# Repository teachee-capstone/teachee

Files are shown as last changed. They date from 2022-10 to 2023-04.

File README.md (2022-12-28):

# TeachEE
This monolithic repository contains all software, RTL, hardware designs, and
reports for the TeachEE oscilloscope capstone project.

Each subdirectory of this repository contains a README explaining its contents.
The repository primarily consists of the software, hardware and rtl
subdirectories. These folders contain the Rust desktop app code, PCB design, and
SystemVerilog code respectively. In addition to these directories, there are also dedicated folders for our reports and miscellaneous files.

# Authors
- [Eric Yang](https://github.com/EYangster)
- [John Giorshev](https://github.com/jagprog5)
- [Timothy Morland](https://github.com/thetimmorland)
- [Ethan Peterson](https://github.com/ethanmpeterson)

# System Block Diagram

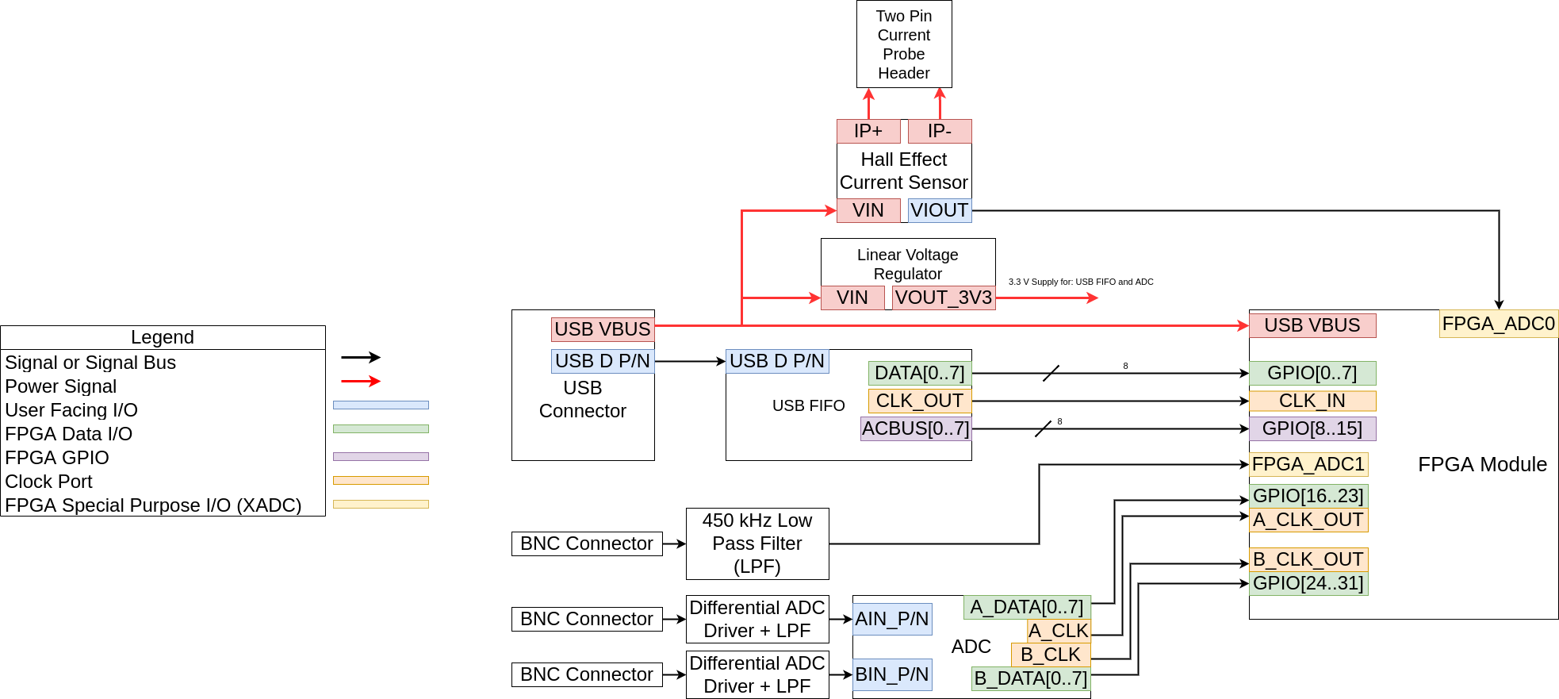
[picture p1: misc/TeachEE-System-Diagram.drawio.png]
Drawio Diagram


# PCB Design
The full design has been uploaded to Altium's online viewer. Click [here](https://365.altium.com/files/0E0F9283-7CE6-4F7A-A1F5-A4D0804C79EE) for
full schematics, layout, and bill of materials.

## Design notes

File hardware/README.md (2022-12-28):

# TeachEE Hardware

The hardware folder is broken down as follows:
- The TeachEE directory contains the Altium schematic and layout files.
- Vendor Communications contains the DFM/DFA related correspondence we had with
  the vendor. (Bittle / 7PCB.com)
- The prints folder holds a variety of reference PDFs including prints of the
  schematics and layout.

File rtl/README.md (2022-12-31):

# TeachEE RTL
This folder contains all the SystemVerilog code for the CMOD A7 35-T FPGA Module
installed on the TeachEE PCB. The subdirectories hold RTL modules for the
oscilloscope firmware as well as some example Vivado projects demonstrating each
module.

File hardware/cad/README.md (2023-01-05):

# CAD
This folder contains the Fusion 360 CAD for the TeachEE PCB enclosure. Currently, it is a simple 3D printed back plate to ensure that board is supported and not exposed to any short circuits when placed on metal surfaces.

The PCB is attached to the tray using M3 screws and heat-set inserts in the tray. Links to the parts are provided below:

- [Heat-set inserts](https://3dprintingcanada.com/products/m3x5-heat-set-brass-knurled-insert-nut-10-pack?variant=39417926451269&ab_version=B&gclid=Cj0KCQiA5NSdBhDfARIsALzs2ECMH8QoEQ02sKMftqXC5ZgHy1LyS_iIIELi0KJeUmQRDeO0tNmDuHEaArR1EALw_wcB)
- [M3x6 Screws](https://www.mouser.ca/ProductDetail/Keystone-Electronics/7689-1?qs=wOxb8XianXi8JqFIUmvR9Q%3D%3D&mgh=1&gclid=Cj0KCQiA5NSdBhDfARIsALzs2EC01tEHi3BZq6HwX3hLjHV2irnkbD29NnEpqoeVlWQxZYohotHjxuUaArSlEALw_wcB)

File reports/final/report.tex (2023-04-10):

\documentclass[letterpaper,11pt]{article}
\usepackage[parfill]{parskip} % Remove paragraph indentation
\usepackage{amsmath}
\usepackage{float}
\usepackage[margin=1in]{geometry}
\usepackage{graphicx}
\usepackage{placeins}
\usepackage{siunitx}
\usepackage[title]{appendix}
\usepackage{pdflscape}
\usepackage{tabularx}
\usepackage{times}
\usepackage{url}
\usepackage{setspace}
\usepackage[none]{hyphenat}
\usepackage{pdfpages}
\usepackage{longtable}
\usepackage{tikz}
\usepackage{hyperref}
\usepackage{minted}

\DeclareSIUnit{\samplepersec}{SPS}
\newcommand{\code}[1]{\mintinline{text}{#1}}

\begin{document}

\begin{titlepage}
    \begin{center}
        \vspace*{1cm}

        \Large
        \textbf{ELEC 490/498 Project Final Report}

        \vspace{0.5cm}
        Group 18\\
        TeachEE: Accessible Electronics Instrumentation\\
        \vspace{0.5cm}
        \normalsize
        \textbf{John Giorshev (20103586, john.giorshev@queensu.ca) \\ Eric Yang (20120750, e.yang@queensu.ca) \\ Ethan Peterson (20105011, 17emp5@queensu.ca) \\ Timothy Morland (20096286, 17tm22@queensu.ca)}\\
        \vspace{0.5cm}
        Submitted April 10, 2023\\

        \vfill
            
        \textbf{To:}\\
        Instructor Dr. Michael Korenberg (korenber@queensu.ca) \\
        Instructor Dr. Alireza Bakhshai (alireza.bakhshai@queensu.ca) \\
        Instructor Dr. Alex Tait (alex.tait@queensu.ca) \\
        Instructor and Supervisor Dr. Sean Whitehall (sw109@queensu.ca) \\
        Supervisor Dr. Thomas Dean (tom.dean@queensu.ca) \\
            
        \vspace{1.8cm}

    \end{center}
\end{titlepage}
\setstretch{1.5}
\pagenumbering{gobble}
\section*{Executive Summary}
% ERIC OWNS THIS SECTION
The Covid-19 pandemic abruptly forced educational institutions towards online
learning. As a result, many of these institutions were unequipped to deal with
this new learning model. Much of the onsite equipment, such as oscilloscopes and
signal generators, is ill-suited for online learning due to its high cost and
poor portability. Additionally, the take-home equipment provided to students
during the pandemic was typically of lower quality in comparison. In particular,
the oscilloscopes provided by the Electronics II course taught at Queen's
University were expensive and of poor quality. They had tiny 3-inch displays and
a small maximum bandwidth of 100 kHz. Moreover, they were single channel,
limiting the student's ability to see how signals in a circuit are related to
one another.

TeachEE is a general-purpose electronics measurement instrument designed for remote
engineering labs, functioning as both an oscilloscope and current monitor. It bundles
together the functionality most required in Electrical Engineering labs and packages
it with lightweight and portable software. 

TeachEE's hardware consists of a four-layer custom designed Printed Circuit
Board (PCB) powered by a USB connection to the computer. The PCB has a
two-channel 1 MSPS ADC for reading low-speed signals and current from a
hall-effect sensor. The PCB also has a two-channel 40 MSPS Analog to Digital
Converted (ADC) for observing high speed signals. Both ADCs are connected to a
Field Programmable Gate Array (FPGA), which is in turn connected to USB 2.0 PHY.
The FPGA collects sample data from both ADCs and frames it into packets, which
are sent over the USB PHY and transmitted to the computer to be decoded and
displayed. This allows TeachEE to leverage the student's machine to create a
streamlined user experience. 

TeachEE's software is a full stack application written in Rust. Its workload is split
between three modules, each of which runs in its own thread. The first module is the
USB Manager, responsible for reading and decoding packets from the hardware driver
into voltage and current samples. The second is the App, responsible for updating and
displaying the user interface. The third module, the Controller, facilitates
communication between the two, and performs signal triggering and frequency spectrum
analysis. These three threads pass samples between each other using two sets of two
buffers: the USB Buffers and App Buffers. By cycling between buffers within a set,
much of the data processing can be parallelized, greatly improving performance. 

\newpage

\setstretch{1}
\tableofcontents
\listoffigures
\listoftables
\newpage
% upgraded this to double spacing as per report formatting reqs
\setstretch{2}
\pagenumbering{arabic}
\section{Motivation \& Background}
% ERIC
% Motivation and background – a clear problem statement and the motivation for the
% project (why is it technologically interesting?). A good motivation argument
% usually relies on facts and figures about the technological void that you seek
% to fill with your design. Back-up your facts and figures by referencing archival
% references. Examples of archival references include: journal papers, conference
% papers, patents, books, corporate technical and annual reports, application
% notes. Use the standard IEEE citation format. Website URLs are not archival
During the Covid-19 pandemic, universities abruptly switched to remote learning
as campuses were shut down. This sudden change exposed the lack of support for
digital learning models \cite{online_learning}. Although the pandemic has since
passed, forward-thinking institutions are starting to invest in online programs,
for example, by leveraging AI chatbots and teaching assistants. Additionally,
online course providers such as Udemy have recently risen in popularity as a
cheap alternative to traditional postsecondary education. With this trend of
remote higher education, engineering students will need their own lab equipment
to complete their learning requirements.

TeachEE is a general-purpose electronics measurement instrument
designed for remotely delivered engineering labs. It acts as both a
USB oscilloscope and current monitor. Currently, there are few instrumentation
options for students completing their labs remotely. The oscilloscopes used for
onsite learning are bulky and difficult to use. TeachEE bundles
together the functionality most commonly required for electrical engineering
labs and packages it with portable software that can run on lower end computers
with any operating system.

As TeachEE is targeted for electrical engineering students, it must be powerful
enough for use in a variety of practices, but also simple and intuitive enough
for novices. It must be compact, to be carried between classes, and
operating-system agnostic, to ensure that students can use it with any machine.
Finally, TeachEE must be cost-efficient, so that students can justify purchasing
this oscilloscope as opposed to alternatives.

\section{Design}
%% Design – describe your functional requirements and constraints; provide
%% technical details about your design process for meeting the project goals;
%% this might include identifying subsystems, analysis, modeling, and key
%% decisions made. If your project involves circuit design, you should describe
%% the simulations used to create your design

% Summarize Design process of hardware, fpga and SW. Make a brief note about how
% we parallelized much of the work by modelling the data as a byte stream.
% allowing for significant dev work without physical HW in house.

The TeachEE design is derived from the system requirements set in the blueprint
report. Given in Table \ref{tab:hw-reqs} and \ref{tab:sw-reqs} are the most important hardware
and software requirements respectively. It should also be noted that the FPGA
shares responsibility with the desktop application for fulfilling software
requirements.

\begin{table}[H]
    \caption{Hardware Requirements}
    \begin{tabularx}{\textwidth}{l|l|l|l}
          & Specification & Target Value & Tolerance \\
        \hline
        1 &Voltage Input Bandwidth&\SI{100}{\kilo\hertz}& $\pm \SI{1}{\kilo\hertz}$ \\
        2 &Current Input Bandwidth&\SI{100}{\kilo\hertz}& $\pm \SI{1}{\kilo\hertz}$ \\
        3 &Number of Current Input Channels& $1$ & $0$ \\ 
        4 &Number of Voltage Input Channels& $1$ & $+2$ \\
        5 &Voltage Sample Rate& \SI{1}{\mega\samplepersec} & \SI{0}{\mega\samplepersec}\\
        6 &Current Sample Rate& \SI{1}{\mega\samplepersec} & \SI{0}{\mega\samplepersec} \\
    \end{tabularx} 
\label{tab:hw-reqs}
\end{table}

\begin{table}[H]
  \caption{Software Requirements}
  \begin{tabularx}{\textwidth}{l|l}
    \textbf{1} & \textbf{Functional Requirements}\\
    \hline
    1.1 & The software shall be able to modify the horizontal and vertical scales of the plot. \\
    1.2 & The software shall be able to modify the trigger voltage. \\
    1.3 & The application shall be deployable to Windows, macOS, and Linux. \\
    \hline
    \textbf{2} & \textbf{Interface Requirements} \\
    \hline
    2.1 & The software shall be able to capture voltage samples and export them to a CSV file. \\
    2.2 & The software shall receive samples via the FTDI 232 in synchronous mode. \\
    \hline
    \textbf{3} & \textbf{Performance Requirements} \\
    \hline
    3.1 & The software shall be able to render waveforms at a rate of \SI{30}{\hertz} on screen.
  \end{tabularx} 
  \label{tab:sw-reqs}
\end{table}

Based on the system requirements, the project is divided into three
subsystems; hardware, FPGA, and software. The following subsections correspond
to each subsystem, each describing the subsystem's top level design and
key design decisions made to comply with system requirements.

% INCLUDE THE BLOCK DIAGRAMS FOR EACH OF THESE
% Talk about old design (from blueprint)
\subsection{Hardware} % Ethan
The primary design driving requirements for the Printed Circuit Board (PCB) are
the bandwidth and sample rate of the data acquisition channels. Bandwidth and
sample rate constrain the selection of the input filters and Analog to Digital
Converters (ADCs) on the PCB. After selecting these parts, they can be easily
duplicated to add additional channels. A full requirement
compliance check for the hardware and other subsystems is provided in Section
\ref{sec:testing}.

Given the requirement for a single voltage and current channel with room for
additional voltage channels, the team settled on a four-channel design. One ADC
channel would be used for current and another for voltage. The remaining two
channels would be made available to be implemented as a stretch goal. The two
spare channels would also have a higher sample rate to improve the utility of
the instrument.

The data acquisition channels are connected to an FPGA rather than a
microprocessor. This decision was made to prevent real time data processing
limitations and ensure precise timing in the sampling of the signal waveforms.
Moreover, an FPGA or ASIC is commonly used in existing commercial
oscilloscopes to fulfill these real time requirements. A compromise that was
made in the design was the use of an FPGA module, rather than installing
the chip to the PCB directly. While such a module could not be used in TeachEE
in a mass-production setting, it greatly shortened the PCB design time, and
allows the FPGA to be easily replaced in the event of hardware failure.
Additionally, the FPGA combines all the sample streams and provides a single
point of contact to the USB interface.

Figure \ref{fig:hw-block-diagram} is a complete hardware block diagram used as a
guide for the PCB design implementation.

\begin{figure}[H]
  \centering
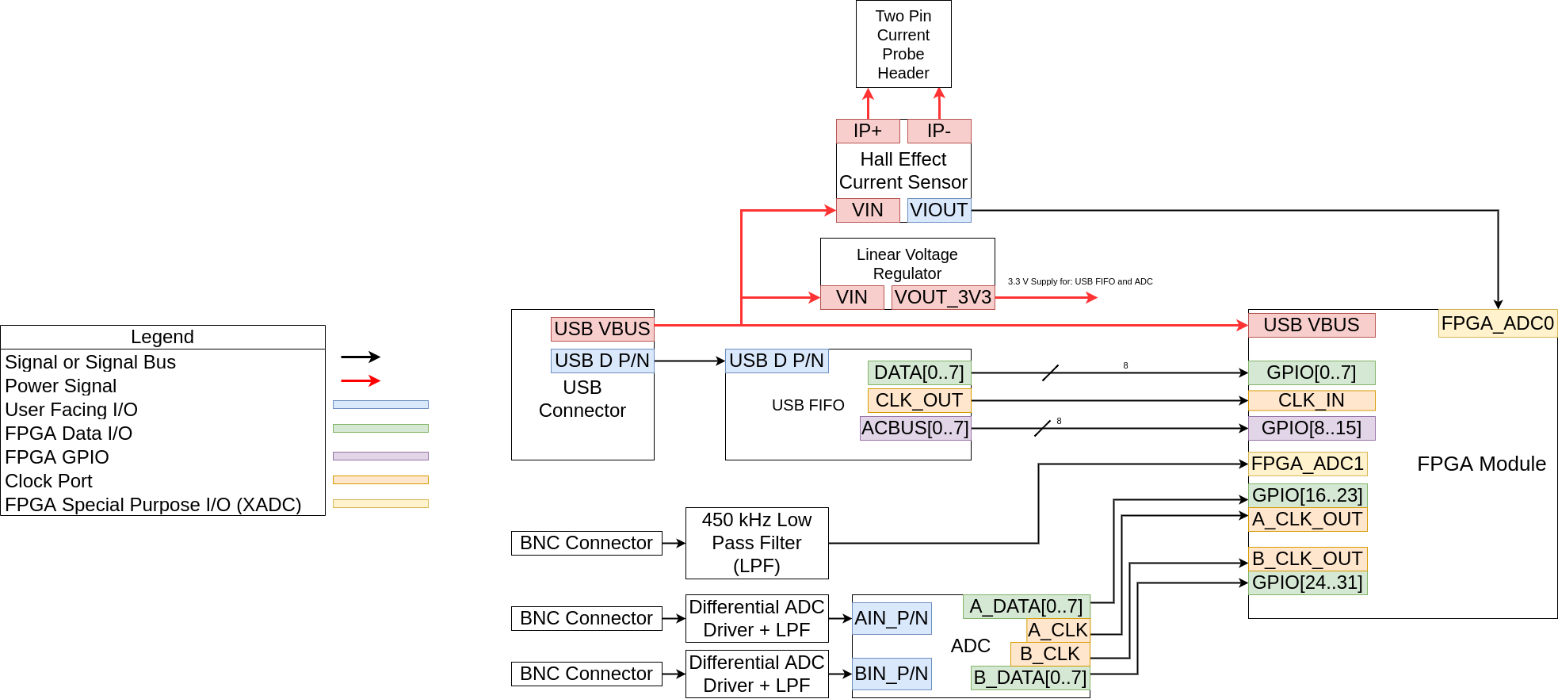
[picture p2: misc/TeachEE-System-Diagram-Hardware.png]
  
  \caption{Hardware System Block Diagram}
  \label{fig:hw-block-diagram}
\end{figure}

\subsection{FPGA} % Ethan
The FPGA RTL is driven by the implicit requirement to send multiple streams of
data with low latency. The sample rate and bandwidth requirements are not as
concerning in the design of the FPGA subsystem. This is because sample rates can
be easily tuned in the FPGA with clock generation PLLs and bandwidth depends on
the analog bandwidth of the input circuitry on the PCB.

In order to transmit multiple streams, the FPGA needs to frame multichannel
data in a standard packet format. A multiplexer is also used in the case that
sending all data at once oversaturates USB 2.0. With these issues
in mind, the diagram given in Figure \ref{fig:fpga-block-diagram} provides a
system-level block diagram for the FPGA design.

\begin{figure}[H]
  \centering
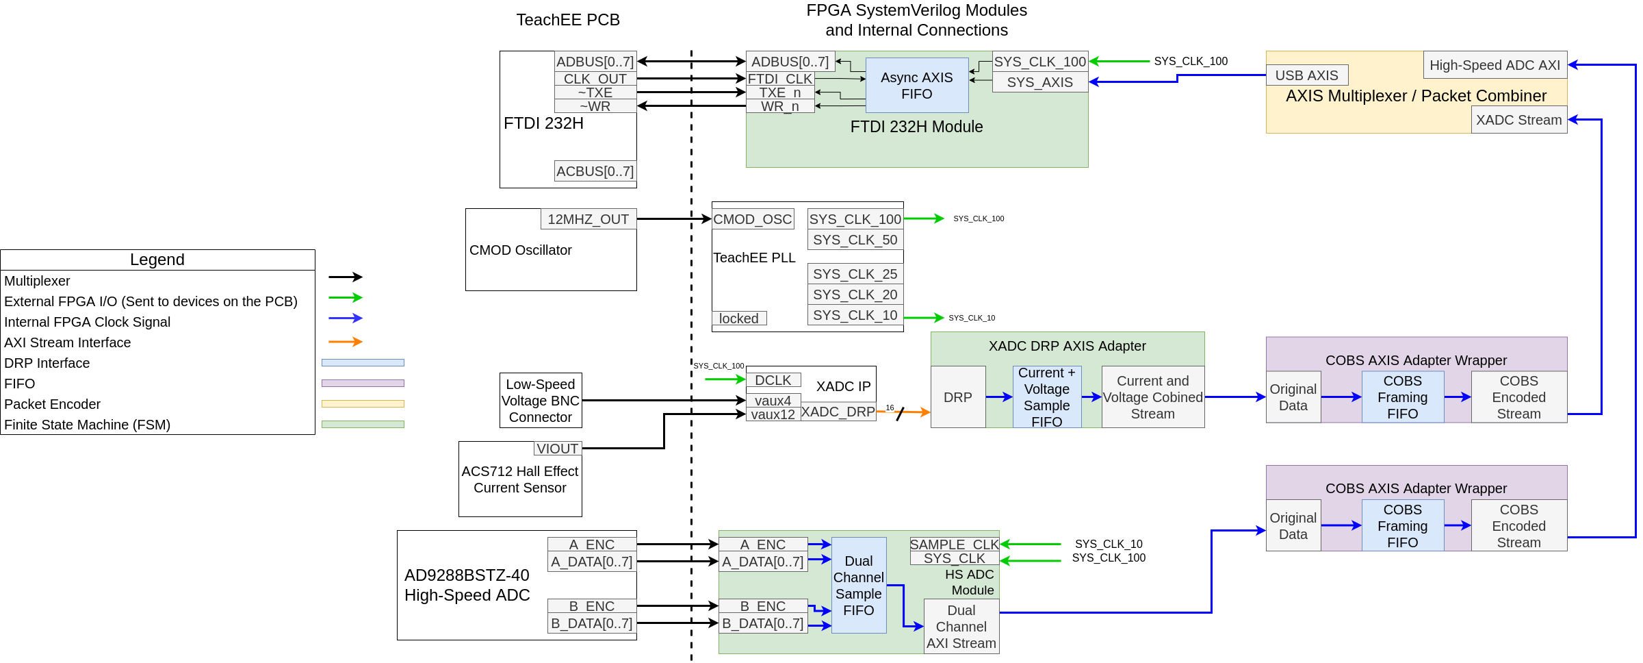
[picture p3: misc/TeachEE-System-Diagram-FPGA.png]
  
  \caption{FPGA System Block Diagram}
  \label{fig:fpga-block-diagram}
\end{figure}

A full breakdown of Figure \ref{fig:fpga-block-diagram} is given in Section
\ref{sec:impl} focusing on implementation. Overall, the initial design is nearly
identical to the final implementation. The team made use of Consistent Overhead
Byte Stuffing (COBS) packet encoding as promised in the blueprint and added a
standard Advanced Extensible Interface (AXI) Streaming protocol for the internal
FPGA datapath.

\subsection{Software} \label{sec:soft-design}% Tim
% Initial design: Tauri, two threaded one buffer guarded with mutex
% Stuff from blueprint with more detail (and from ECE night)

Several iterations were required to complete TeachEE's desktop application.
Initially, the prototype was built using the Tauri GUI framework. Tauri was
selected since it uses an instance of the Chrome Web Browser to render the user
interface, allowing developers to take advantage of the rich library and
tooling ecosystem for frontend web development. Despite these benefits, two
major factors necessitated a change: 1) displaying a rapidly changing
waveform using HTML and JavaScript at the required \SI{60}{\hertz} frame rate
proved extremely difficult; 2) data transfer between Rust and JavaScript
resulted in increased code complexity.

\code{egui} was selected as a replacement for Tauri because of its simple API
and large built-in widget library. \code{egui} is an \emph{immediate mode}
GUI, meaning it re-renders all widgets on every frame, regardless of whether or
not the application state had changed. This technique sacrifices
efficiency for a simpler programming model in which a developer expresses their
GUI as a single pure function \(f:~\text{State}~\mapsto~\text{UI}\)
\cite{egui}. An \emph{immediate mode} GUI is a good fit for TeachEE, since its
UI changes frequently and independently of user-input, nullifying the
aforementioned efficiency problem; even with a traditional \emph{retained mode}
GUI, widgets would still re-render whenever a new voltage/current is received.

Later in the software design process, performance issues were encountered
related to processing the incoming data stream fast enough to update the GUI at
\SI{30}{\hertz}. The slowdown was caused by the original threading model, in
which the USB Manager and App threads communicated via a single
shared buffer protected by a mutex. When the App thread attempted to
render a new frame, it would frequently be blocked by the USB Manager, which
was simultaneously writing incoming samples. The frequency and duration of this
blocking behaviour was prevalent enough to greatly reduce frame rate. To address
this problem, the software was reimplemented using the three thread
design described in Section \ref{sec:software-impl}.

\section{Implementation} \label{sec:impl}
%% Describe how the solution was implemented – this may involve a description of
%% major code blocks, schematics, photographs, CAD drawings, etc. The reader
%% should understand the materials and operation of your implemented project,
%% and the tools (hardware and/or software) used. This should also include a
%% full bill of materials and final project budget.

% Discuss how everything was implemented here
% Ethan will include figure of top level altium schematic
% Ethan will also include snippet of the top level SystemVerilog Module.
% I will pull in full schematics, layout and code into the appendices

The implementation is broken up into three subsections corresponding to each
subsystem.

\subsection{Hardware} % ETHAN
The hardware solution for TeachEE is implemented in the form of a four-layer
PCB. The PCB is designed using the Electronic Design Automation (EDA) software
Altium Designer, the industry standard tool for PCB design. Our design takes
advantage of Altium's hierarchical schematics, allowing the schematic to be
broken up into multiple pages with interconnects between the different
sub-circuits. TeachEE's top level schematic is an interconnect between all the
sub-circuits of the PCB, and is shown in Figure \ref{fig:hw-top-level-sheet}.
All eight pages of the schematic are provided in Appendix
\ref{appendix:schematic}.

\begin{figure}[H]
  \centering
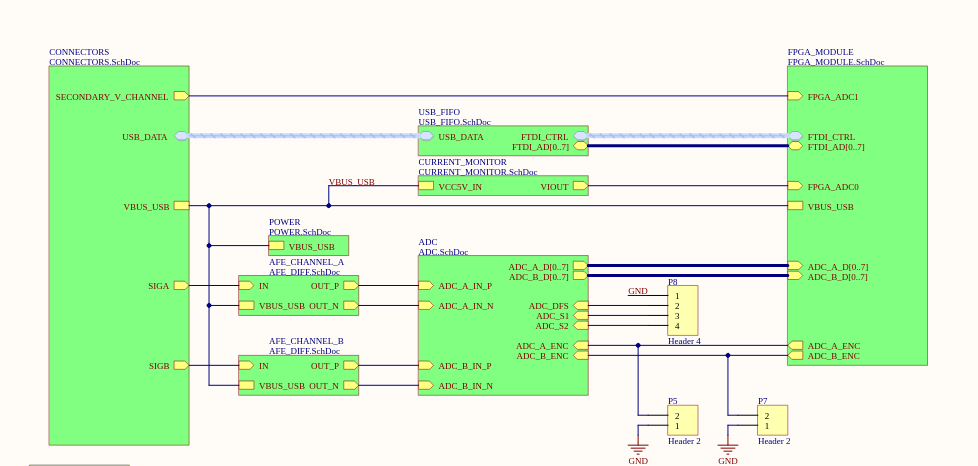
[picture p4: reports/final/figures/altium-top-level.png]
  
  \caption{TeachEE PCB Top Level Schematic}
  \label{fig:hw-top-level-sheet}
\end{figure}

The following subsections break down each sub-circuit sheet entry in Figure
\ref{fig:hw-top-level-sheet}.

\subsubsection{Power}
The power schematic sheet contains a single LD1117V33C linear voltage regulator.
The regulator takes the \SI{5}{\volt} VBUS supply from the USB connection and
provides a \SI{3.3}{\volt} power output. A linear voltage regulator is employed
over a switching buck converter for the following reasons:
  \begin{enumerate}
    \item The analog to digital converters require clean voltage references to
      produce accurate readings and function correctly. Buck converters
      typically have noisier outputs that could harm performance.
    \item The linear voltage regulator requires fewer components to implement,
      easing chip shortage concerns.
    \item The significantly lower efficiency of a linear regulator is not an
      issue as this regulator has a capacity of \SI{1}{\ampere}, which is more
      than enough to run the devices on board.
  \end{enumerate}

\subsubsection{USB FIFO}
The USB FIFO is a queue that sends data out to the laptop over USB 2.0 Full
Speed (FS), capable of up to 480 Mbps. This circuit takes a
parallel byte stream from the FPGA and converts it to a USB 2.0 data stream. The
FT232HQ USB FIFO made by FTDI is used to implement this functionality. This chip
was selected over other USB Interface ICs for the following reasons:
  \begin{enumerate}
    \item Availability. USB Interfaces are one of many ICs in short supply
      in the ongoing chip shortage. In fact, this IC was ordered for the
      project after ELEC390 in July 2021 and only received in August 2022.
    \item Extensive preexisting software tooling. FTDI provides a driver and
      configuration utility for extracting data from their USB interfaces. This
      significantly reduces the software development work required to build a
      sample streaming interface. This ease of use is critical in a project with
      such a short timeline.
  \end{enumerate}

For debugging and circuit visibility, all digital control signals on the
FT232HQ are connected to test points. The schematic sheet also contains some
surrounding circuitry in the form of power filtering, a clock oscillator, and
configuration EEPROM.

\subsubsection{Current Monitor}
The current monitor page contains a hall effect current sensor circuit. The
circuit uses the ACS720KLATR current sensor. This sensor was chosen due
to its supply chain availability and the fact that it reports its reading
through a voltage output. The voltage output is linearly proportional to the
current flowing through the sensor plus a DC offset. This is a preferable
interface as it can be connected to an ADC channel without having to write
a new driver for the specific sensor on the FPGA. As such, the output of
the current sensor is connected to FPGA\_ADC0, which is one of two ADC channels
available on the FPGA module.

\subsubsection{ADC}
The TeachEE ADC schematic sheet contains an AD9288BSTZ dual channel
\SI{40}{\mega\samplepersec} ADC. This chip provides two additional high-speed
voltage channels in addition to the ADC channels provided by the FPGA
module. The data outputs for channels A and B are sent to the FPGA along
with the sample clocks. This ADC was selected for its FPGA friendly control
interface. Since the control consists of only a data bus and sample clock, it is
trivial to write an FPGA module to collect the data in comparison to other SPI
and I2C based converters on the market.

Bypass capacitors and ferrite beads are used to power the ADC for the cleanest
reference voltage possible. Additionally, the PCB contains non-populated
footprints for low pass filters, and filter bypasses to simplify testing and
debugging. For the digital side, all data busses and clocks have test points so
multimeters or oscilloscopes can be connected to debug the FPGA control signals.

\subsubsection{Analog Front End (AFE)}
The Analog Front End (AFE) sits in front of the inputs of the high-speed ADC. As
a result, this sub-circuit is duplicated twice in the top level sheet shown in Figure
\ref{fig:hw-top-level-sheet} to cover both channels. The AFE serves the following
purposes in the data acquisition hardware.

\begin{enumerate}
  \item Protect the ADC from over-voltage conditions. The front-end must clamp
    any voltages that would otherwise destroy the ADC.
  \item Convert the signal from single ended to differential. The ADC takes in a
    differential input, so the AFE must convert the input voltage observed at
    the connector to a differential signal of equivalent magnitude.
\end{enumerate}

This functionality is implemented in hardware using an AD8138 differential ADC
driver. This all-in-one component takes care of voltage clamping and
single-to-differential conversion. Moreover, it has sufficient analog bandwidth
to avoid reducing the effective bandwidth of the ADC. For debugging, the
sub-circuit contains 0-ohm bypass resistors that can be optionally soldered to
send the unclamped signal directly to the ADC.

\subsubsection{FPGA Module}
The FPGA module is implemented using a CMOD A7-35T Xilinx Spartan 7 Breakout
Board. It is connected to the PCB via two 28-pin headers. Two pins are
used for power and ground while the rest are used for FPGA IO pins. The USB FIFO
and ADC control pins are connected to the FPGA IO. There are also two special pins
which can be used as ADCs. These two pins are used to implement the current and
voltage channels at 1 MSPS. The current sensor output is wired to one of the
channels and a BNC connector is connected to the other through a low pass filter
for voltage sampling.

The FPGA module schematic had one mistake that was not discovered until the
physical PCBs had already been manufactured and delivered. To use the
parallel-bus interface of the FT232HQ to send data, the FPGA must lock to a
\SI{60}{\mega\hertz} output clock from the FT232HQ. During layout, the FPGA pin
wired to this clock was swapped to a normal GPIO pin rather than a Multi Region
Clock Capable (MRCC) pin. As a result, the FPGA place and route was failing
during compilation, as the FPGA could not route this clock from a standard GPIO
pin. This issue was resolved by waiving the warnings and optimizing the
SystemVerilog code to still pass timing without a proper clock route for the
\SI{60}{\mega\hertz} signal. Further information on this process is given in
Section \ref{sec:fpga-impl}.

\subsubsection{Connectors}
% Talk about LPFs and BNC connectors 
The connectors page contains all the external IO connections for TeachEE.
Specifically, the USB mini connector for data and three BNC connectors for scope
probes. The current sensor is exposed on its own separate pin header. The BNC
connectors are connected to the appropriate ADC input or AFE. Also, each
connector has the appropriate low pass filters to satisfy Nyquist's theorem. Each
connector also includes all the standard capacitors and resistors needed to
connect an oscilloscope probe from the lab kit sold at the Queen's bookstore.
\subsection{FPGA} \label{sec:fpga-impl} % ETHAN
% Refer to system block diagram and go module by module.
% put in the top level module code and some critical state machines
% Talk about AXIS as a standard protocol. Also the extensible to ARM SOCs it
% provides

The FPGA datapath and implementation can be summarized by examining the
interconnections between modules in the top level SystemVerilog module. Below is
each section of the top level TeachEE RTL module broken down and explained. The
entire RTL codebase can be viewed in Appendix \ref{appendix:rtl-code}.

\subsubsection{Top Level Module Interface}
Given below is the interface to the top level module of the TeachEE RTL code.

\setstretch{1}
\begin{minted}{systemverilog}
module teachee (
  input  var logic cmod_osc, // 12 MHz provided on the CMOD
  input  var logic ftdi_clk, // 60 MHz provided by the FTDI

  // FTDI Control Interface
  input  var logic ftdi_rxf_n,
  input  var logic ftdi_txe_n,

  output var logic ftdi_rd_n,
  output var logic ftdi_wr_n,
  output var logic ftdi_siwu_n,
  output var logic ftdi_oe_n,

  output var logic[7:0] ftdi_data,

  // High Speed ADC IO Interface
  output var logic hsadc_a_enc,
  input var logic[7:0] hsadc_a,

  output var logic hsadc_b_enc,
  input var logic[7:0] hsadc_b,

  input var logic[1:0] xa_n,
  input var logic[1:0] xa_p,
  ...
);
\end{minted}
\setstretch{2}

As shown above, the FPGA takes in a \SI{12}{\mega\hertz} clock provided by an
external oscillator and the \SI{60}{\mega\hertz} clock from the FT232HQ. After
the clocks, IO for the FT232HQ and AD9288BSTZ control signals are defined. Some
additional pins spare pins and LED signals at the end of the interface
declaration are not shown as they were used for debugging purposes.

\subsubsection{PLL Clock Generation}
After the module interface is declared, the PLL system clock generator is
initialized. This is an IP core provided by the FPGA manufacturer Xilinx that
takes the oscillator \SI{12}{\mega\hertz} input and outputs a variety of useful
clock signals for the rest of the design. Given below is the IP core module
instantiation.

\setstretch{1}
\begin{minted}{systemverilog}
    teachee_pll teachee_pll_ip_inst (
        // Clock out ports
        .clk_100(clk_100),     // output clk_100
        .clk_50(clk_50),     // output clk_50
        .clk_25(clk_25),     // output clk_25
        .clk_20(clk_20),     // output clk_20
        .clk_10(clk_10),     // output clk_10

        // Status and control signals
        .reset(0), // input reset
        .locked(locked),       // output locked

        // Clock in ports
        .cmod_osc(cmod_osc)      // input cmod_osc
    );
\end{minted}
\setstretch{2}

The module takes the external oscillator clock as an input and outputs 100, 50,
25, 20 and \SI{10}{\mega\hertz} clocks. Different frequencies can be specified
within the Xilinx Vivado IDE used to flash the FPGA. In the current
implementation, only the 100 and \SI{10}{\mega\hertz} clocks are used.
\SI{100}{\mega\hertz} is used throughout the top level system and
\SI{10}{\mega\hertz} is used as a sampling clock in the high speed ADC. One
clock that is not covered by this PLL is the \SI{60}{\mega\hertz} clock
generated externally by the FT232HQ. The PLL also has a \code{locked} output.
When driven high, this signal indicates that the PLL is locked to the input
clock and the output clocks are functioning correctly. This signal is used to
send a reset signal to all modules, holding them in reset until the PLL has
locked and all clocks are up and running.

\subsubsection{Interface Instantiations} \label{sec:interface-inst}

Given below are the instantiations for the different interfaces used to make
connections between the submodules. Interfaces in SystemVerilog can be thought
of as groupings of wires that make managing inter-module connections easier as
each wire does not need to be explicitly declared.

\setstretch{1}
\begin{minted}{systemverilog}
    hsadc_interface hsadc_ctrl ();
    ...
    axis_interface #(
        .DATA_WIDTH(2 * XADC_DRP_DATA_WIDTH)
    ) xadc_sample_channel (
        .clk(sys_clk),
        .rst(reset)
    );

    axis_interface #(
        .DATA_WIDTH(16)
    ) hsadc_sample_channel (
        .clk(sys_clk),
        .rst(reset)
    );
\end{minted}
\setstretch{2}

The first interface declared is for the AD8138ARZ high-speed ADC. External IO
signals are assigned to the different control wires in the interface. Next, the
various AXIS interfaces required to connect the modules are instantiated. The
interface width is specified using the \code{DATA_WIDTH} parameter. 8-bit
interfaces are used to connect the packet stream output for a given ADC to the
FT232HQ wrapper module that adapts the AXI Stream to FT232HQ control signals.
The remaining two interfaces hold the sample data from the XADC and high-speed
ADC respectively. The XADC is the dual channel 16-bit ADC built into the FPGA.
The two sample data interfaces \code{hsadc_sample_channel} and
\code{xadc_sample_channel} are each connected to the outputs of adapter modules
that adapt the native interface of the device to an AXI Stream. The AXI Stream
interface used is a custom wrapper for all the standard signals found in an AXI
stream. The interface definition can be found in Appendix
\ref{appendix:axis-interface}.

The AXIS Protocol, also known as AXI Stream, is derived from ARM's AXI bus
specification. Additional information on the AXI Stream protocol and the
external libraries used to support it can be found in Section
\ref{sec:external-fpga-libs}.

\subsubsection{FT232HQ AXIS Wrapper}
After instantiating the interfaces, they are used to make connections between
the various submodules. Shown below is the \code{ft232h} module instance used
to send data to the computer over USB.

\setstretch{1}
\begin{minted}{systemverilog}
    ft232h usb_fifo (
        .ftdi_clk(ftdi_clk),

        .ftdi_rxf_n(ftdi_rxf_n),
        .ftdi_txe_n(ftdi_txe_n),

        .ftdi_rd_n(ftdi_rd_n),
        .ftdi_wr_n(ftdi_wr_n),
        .ftdi_siwu_n(ftdi_siwu_n),
        .ftdi_oe_n(ftdi_oe_n),

        .ftdi_adbus(ftdi_data),

        // Programmer AXIS Interface
        // CHANGE THIS BASED ON WHETHER YOU WANT TO USE XADC OR HSADC
        .sys_axis(xadc_usb_axis.Sink)
    );
\end{minted}
\setstretch{2}

This module consists of a state machine that adapts the AXI Stream of sample
packets to control signals of the FT232HQ. The input is the \code{sys_axis}
stream and the output is all the \code{ftdi_*} control signals used to produce
data over USB. Wrapping the FT232HQ interface in a standard AXI Stream makes it
trivial to interface with all the other modules in the TeachEE source code. The
same design approach is used throughout the codebase to ensure compatibility
between the various hardware interface modules. The state machine for the module
is shown in Figure \ref{fig:ft232h-state-machine}.

\begin{figure}[H]
  \centering
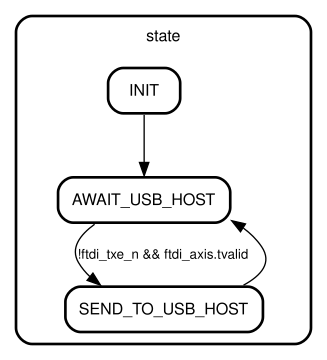
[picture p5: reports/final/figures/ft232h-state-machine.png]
  
  \caption{FT322H AXI Wrapper State Machine}
  \label{fig:ft232h-state-machine}
\end{figure}

The state machine waits for the AXI Stream to have data available and for the
FT232HQ to be ready for new data. When this condition is satisfied, the byte is
sent out and the state machine automatically transitions back to the await
state.

Regarding the comment in the code above about changing the \code{sys_axis}
stream input, in this case, the XADC is used.

\subsubsection{XADC IP Core}
Shown below is the XADC IP core used to extract data from the internal XADC on
the FPGA. This IP core is made custom using the XADC Wizard tool in Xilinx
Vivado. The core is configured to only output the two FPGA ADC channels in use
on the TeachEE PCB via a Dynamic Reconfiguration Port (DRP) interface. The DRP
signals are then fed into an AXIS adapter module for interface standardization.

\setstretch{1}
\begin{minted}{systemverilog}
    xadc_teachee xadc_teachee_inst (
        // Clock and Reset
        .dclk_in(sys_clk),          // input wire dclk_in
        .reset_in(reset),        // input wire reset_in

        // DRP interface
        .di_in(0),              // input wire [15 : 0] di_in
        .daddr_in(xadc_daddr),        // input wire [6 : 0] daddr_in
        .den_in(xadc_den),            // input wire den_in
        .dwe_in(0),            // input wire dwe_in
        .drdy_out(xadc_drdy),        // output wire drdy_out
        .do_out(xadc_do),            // output wire [15 : 0] do_out

        // Dedicated analog input channel (we do not use this)
        .vp_in(0),              // input wire vp_in
        .vn_in(0),              // input wire vn_in

        // analog input channels, vaux4 is pin 15 = VIOUT of current sensor
        // vaux12 is pin 16 = low speed voltage channel.
        .vauxp4(xa_p[0]),            // input wire vauxp4
        .vauxn4(xa_n[0]),            // input wire vauxn4
        .vauxp12(xa_p[1]),          // input wire vauxp12
        .vauxn12(xa_n[1]),          // input wire vauxn12

        // conversion status signals
        .channel_out(),  // output wire [4 : 0] channel_out
        .eoc_out(),          // output wire eoc_out
        .alarm_out(),      // output wire alarm_out
        .eos_out(xadc_eos),          // output wire eos_out
        .busy_out()        // output wire busy_out
    );
\end{minted}
\setstretch{2}

\subsubsection{ADC AXIS Wrappers}
Similarly to the \code{ft232h} module, both the XADC and high-speed ADC have
AXIS wrapper modules. Both wrapper modules function in the same manner, they
await new data from the ADC and place it in AXIS compliant FIFO queues. The
\code{sample_stream} output is internally connected to this queue where samples
can be consumed by the FT232HQ. Given below is the instantiation of both
modules.

\setstretch{1}
\begin{minted}{systemverilog}
    xadc_drp_addr_t xadc_daddr;
    var logic xadc_den;

    var logic xadc_drdy;
    var logic[XADC_DRP_DATA_WIDTH-1:0] xadc_do;
    var logic xadc_eos;

    xadc_drp_axis_single_stream xadc_drp_axis_adapter_inst (
        .xadc_dclk(sys_clk),
        .xadc_reset(reset),

        // DRP and Conversion Signals
        .xadc_daddr(xadc_daddr),
        .xadc_den(xadc_den),
        .xadc_drdy(xadc_drdy),
        .xadc_do(xadc_do),

        .xadc_eos(xadc_eos),

        .sample_stream(xadc_sample_channel.Source)
    );

    hsadc_axis_wrapper hsadc (
        .sample_clk(clk_10),
        .stream_clk(sys_clk),
        .reset(reset),

        .hsadc_ctrl_signals(hsadc_ctrl.sink),
        .sample_stream(hsadc_sample_channel.source)
    );

\end{minted}
\setstretch{2}

The XADC wrapper takes in the DRP control signals from the XADC IP core and the
high-speed ADC wrapper gets all the control signals from a single interface
declared earlier in the file.

\subsubsection{AXIS and Verilog AXIS} \label{sec:external-fpga-libs} AXIS, also
referred to as AXI Stream, is the standard protocol used throughout the FPGA
datapath. While there are many signals in an AXI interface, the primary signals
are called \code{tdata}, \code{tready}, and \code{tvalid}. Only when \code{tready}
and \code{tvalid} are asserted can data be consumed from the \code{tdata} bus.
\code{tready} is controlled by the receiver so that it can regulate the rate at which
it consumes data, while \code{tvalid} is controlled by the sender to notify the
receiver when new data is ready on the \code{tdata} lines. The full
specification contains many additional signals, but these three are the ones most
often manipulated during data transmission \cite{axis_spec}. Figures
\ref{fig:axis-read} and \ref{fig:axis-write} show the AXIS read and write timing
diagrams respectively.

\begin{figure}[H]
  \centering
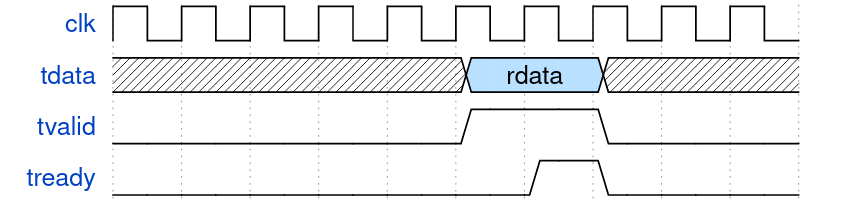
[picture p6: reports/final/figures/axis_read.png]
  
  \caption{AXIS Read Transaction Timing Diagram}
  \label{fig:axis-read}
\end{figure}

In AXIS read and write transactions, the producer is responsible for
\code{tdata} and \code{tvalid} signals while the consumer toggles \code{tready}.
This allows the consumer to know when new data becomes available and it is able
to signal to the producer when it is ready to accept it via \code{tready}. All
three signals should only be asserted or deasserted in synchronization with the
system clock, as per the specification. As shown in Figure \ref{fig:axis-read},
\code{tvalid} is asserted on the same rising edge as the new data coming onto
the \code{tdata} bus. The consumer sees this and asserts tready on the next
rising edge consuming the data. In the case where multiple words of data are
queued by the producer, the \code{tdata} value will advance to the next byte
available after each cycle where both \code{tvalid} and \code{tready} are
asserted. This allows a new read to take place every cycle if the producer has
the data and the consumer is ready for it. This simple protocol yields strong
performance and flexibility with minimal FPGA Lookup Table (LUT) resources used.
It should be noted that for any AXIS transaction to take place, \code{tready} and
\code{tvalid} must both be true.

\begin{figure}[H]
  \centering
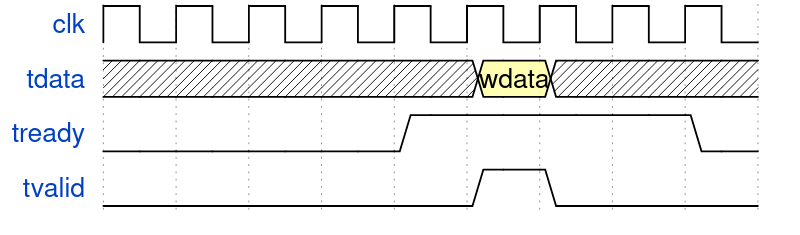
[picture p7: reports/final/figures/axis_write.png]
  
  \caption{AXIS Write Transaction Timing Diagram}
  \label{fig:axis-write}
\end{figure}

In the AXIS write case shown in Figure \ref{fig:axis-write}, the consumer first
asserts \code{tready}, which tells the producer that it can accept new data.
Once the producer has data, it asserts the value on \code{tdata} and drives
\code{tvalid} high on the same rising edge. Since \code{tready && tvalid} is
true, the data is written to the consumer successfully. This design pattern is
replicated repeatedly throughout the FPGA codebase provided in Appendix
\ref{appendix:rtl-code}.

In addition to the simplicity of the protocol, there is significant library support for
AXI Streams. In the case of TeachEE, the \code{verilog-axis} library is used
\cite{verilog_axis_lib}. This library contains a variety of useful Verilog
modules, all of which expose an AXIS interface at their inputs and outputs. The
standard interface across all modules trivializes connecting up the library modules
with TeachEE modules. The only modification made to these library
modules was to wrap them in another more ergonomic module. Since the library is
written in Verilog, it does not have access to interfaces, which are a feature
of SystemVerilog only. As a result, each AXIS signal is written out individually
making instantiating and connecting the modules unwieldy. To bundle all
these signals into one module port, the \code{axis_interface} is used. For each
module in the \code{verilog-axis} library used by TeachEE, a wrapper module is
written that places all the signals for the AXI Streams in AXIS interfaces,
making module connectivity far simpler with SystemVerilog. This is possible
due to the Xilinx Vivado project build configuration that cross compiles both
Verilog and SystemVerilog. The interface is also designed to seamlessly handle
the producer and consumer cases discussed above using modports. The
\code{Source} modport can be used on producer stream interfaces and the
\code{Sink} modport can be used for consumers. The modports switch the direction
of the signals from \code{input} to \code{output} depending on the use case.

\code{verilog-axis} contains many modules but there are three that were employed
when writing the RTL code for TeachEE. 

The first module is \code{axis_async_fifo}, which is wrapped by
\code{axis_async_fifo_wrapper}. This module constructs a First-In-First-Out
(FIFO) Queue and is used repeatedly throughout the code. The first and foremost
purpose of the Queue is to provide sample memory to ensure samples are not
dropped when the rate of production deviates from the rate of consumption.
Secondly, the FIFO is asynchronous, meaning it can use different clock signals
for its input and output. The module has internal synchronization logic to bring
data across clock domains. This functionality was critical in the TeachEE RTL
design as there were multiple clock domains that needed efficient data transfer between
them. The top-level system, USB FIFO, HSADC, and XADC all had different
clock signals and had their data inputs buffered by asynchronous FIFOs.

The second key module is the \code{axis_adapter}, which is wrapped by
\code{axis_adapter_wrapper}. This module takes an AXI Stream and adapts it to a
smaller width specified as a parameter in the module instantiation. This module
was critical in getting the 32-bit sample stream from the XADC to fit the 8-bit
stream accepted by the USB FIFO.

The final module used from the library was \code{cobs_encode}, which is wrapped
by \code{cobs_encode_wrapper}. This module takes an 8-bit input stream and
outputs the same data encoded using COBS. The COBS encoder is highly efficient
and only creates two additional bytes of overhead, minimizing USB link bandwidth
wastage \cite{cobs}. To transmit samples to the computer, the 32-bit stream from
the XADC (or 16-bit from the HSADC) is adapted to 8 bits using
\code{axis_adapter}. The resulting 8-bit stream is fed into the COBS encoder,
whose output is connected to the USB FIFO. These two modules make up the packet
encoding stack.

Perhaps the most important benefit of AXIS over other streaming interfaces is
its direct compatibility with the more fully-featured AXI bus. AXI is a standard
memory-mapped bus interface used in ARM processors \cite{axi_spec}. Since all
modules in TeachEE's FPGA codebase use AXI Streams, the platform is highly
extensible and can be connected to ARM coprocessors with minimal effort. Such a
design extension would make TeachEE architecturally similar to more expensive
benchtop oscilloscopes that make use of both an ASIC and traditional processor
through a high-speed interconnection protocol. An example of this architecture
is Keysight's MegaZoom ASIC \cite{keysight_megazoom}.

\subsection{Software} \label{sec:software-impl} % ERIC 
TeachEE's software workload is split between three modules, each of which runs in its
own thread. The first module is the USB Manager, responsible for reading and decoding
packets from the hardware driver. The second is the App, responsible for updating and
displaying the user interface. Finally, the Controller facilitates communication between
the two and provides additional sample processing.

The software for TeachEE follows an improved threading model described in
Figure \ref{fig:soft-sequence-diagram} below. This design change was necessitated
by software performance issues encountered in the initial design, described in
Section \ref{sec:soft-performance-issues}. The USB manager and Controller share one set of
two buffers, referred to as the USB Buffers, and the App and Controller share
another set of two buffers, the App buffers. The threads coordinate their workflows
such that each thread can exclusively operate on a buffer at a time. For example,
while the USB Manager is writing samples to USB Buffer 0, the Controller can copy
samples from USB Buffer 1 to App Buffer 1, and the App can read from App Buffer 0.
After every work cycle, each thread swaps to the other buffer. This protocol
parallelizes the workload as much as possible and minimizes thread block times.

\begin{figure}[H]
  \centering
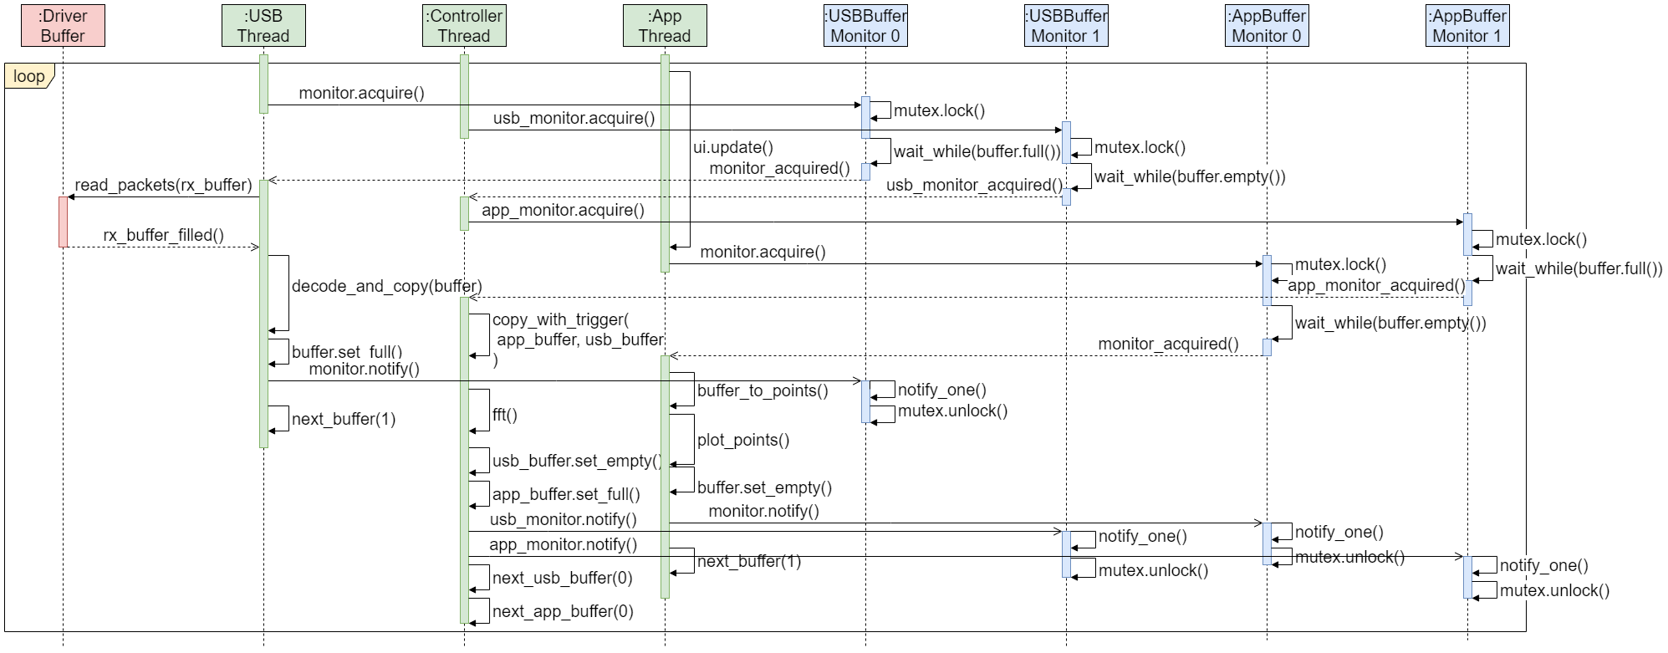
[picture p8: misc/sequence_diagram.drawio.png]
  
  \caption{Threading Model Sequence Diagram}
  \label{fig:soft-sequence-diagram}
\end{figure}

The sequence diagram above simplifies the buffer representation. Each buffer in the
two sets actually represents several buffers/channels in the \code{Channels}
struct. In the current implementation, two channels are supported and every buffer
operation operates on both channels simultaneously. Furthermore, each \code{Channels}
struct is wrapped in a \code{BufferState} enum, representing the emptiness/fullness
of the channels, which in turn is guarded by a monitor. To allow these monitors to
be shared between threads, they are wrapped by Rust's shared pointer, the \code{Arc}.
Figure \ref{fig:soft-buffer-config} below illustrates the shared data's configuration.
Note that there is an additional field in the \code{Channels} struct used to store the
results of frequency spectrum analysis performed in the Controller thread. This field
is unused in the USB Buffer \code{Channels}.

\begin{figure}[H]
  \centering
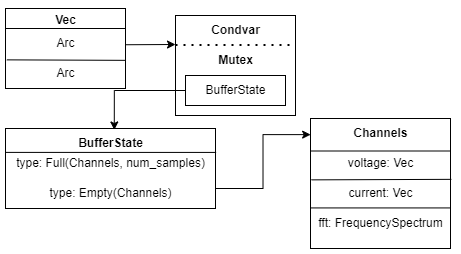
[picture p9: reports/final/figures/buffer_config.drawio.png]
  
  \caption{Shared data configuration representing one set of ``buffers"}
  \label{fig:soft-buffer-config}
\end{figure}

In Rust, a monitor is implemented as a condition variable and mutex tuple. The condition
variable allows threads to wait while a condition is true. The mutex ensures that only
one thread is allowed access to a given \code{Channels} at a time. A thread acquires a
monitor by first locking the mutex. Once the mutex is locked, the thread checks the
\code{BufferState}. If the thread intends to write to the buffers, but the buffers are
\code{Full}, it unlocks the mutex and goes to sleep until it receives a notification
that the buffers have been emptied. The same applies to threads attempting to read from
\code{Empty} buffers. Once the thread is notified, it is woken from the wait function
with the mutex reacquired. A thread releases a monitor by setting the \code{BufferState}
to the appropriate type and notifies a thread waiting on the condition variable. The
mutex is unlocked implicitly when it goes out of scope. An example of this procedure
(run by the App thread) is given in the code block below.

\setstretch{1}
\begin{minted}{rust}
  // Wait until controller thread has filled the current buffer.
  let mut buf_state = condvar
      .wait_while(mutex.lock().unwrap(), |buf_state| buf_state.is_empty())
      .unwrap();
  // Get the Channels buffers.
  let (channels, num_samples) = buf_state.unwrap();
  ...
  // Release the monitor.
  *buf_state = BufferState::Empty(channels);
  condvar.notify_one();
\end{minted}
\setstretch{2}

\subsubsection{The USB Manager}
The USB Manager thread reads packets from the FTDI receiver queue into a buffer,
decodes them into voltage and current samples, and populates the USB Buffers.
The packets are read from the queue using an FTDI library. The thread always
reads 120 000 bytes at a time so that after decoding, the App displays
approximately 20 000 samples each cycle. This ensures that the plotted waveform
does not expand or contract in the horizontal direction, which improves the
user's experience.

The decoding function decodes the six-byte COBS packets into pairs of voltage
and current samples. The main decoding loop is described in the code below.

\setstretch{1}
\begin{minted}{rust}
  ...
  'outer: while src_index + PACKET_SIZE < end
      && dst_index < channels.voltage1.len()
  {
      // Packet error: offset byte not in [1, 5] or packet not delimited
      // with 0
      if self.rx_buf[src_index] == 0
          || self.rx_buf[src_index] >= PACKET_SIZE as u8
          || self.rx_buf[src_index + PACKET_SIZE - 1] != 0
      {
          // Find the next 0 and continue from there
      } else {
          let packet = &self.rx_buf[src_index..(src_index + PACKET_SIZE)];
          let mut block = packet[0] - 1;
          // Two bytes of packet overhead
          let mut decoded: [u8; PACKET_SIZE - 2] = [0; PACKET_SIZE - 2];
          let mut decoded_index = 0;

          // Note: the packet index is just the decoded_index + 1 (skip
          //       the first offset byte)
          // Example packet: 01 02 22 02 44 00
          // Decodes to:        00 22 00 44
          while decoded_index < decoded.len() {
              if block > 0 {
                  decoded[decoded_index] = packet[decoded_index + 1];
              } else {
                  decoded[decoded_index] = 0;
                  block = packet[decoded_index + 1];
              }
              decoded_index += 1;
              block -= 1;
          }

          // Map digital values with 4096 discrete levels to samples
          channels.voltage1[dst_index] =
              (((decoded[3] as u16) << 4) | decoded[2] as u16) as f64
                  * 3.3 / 4095.0;
          channels.current1[dst_index] =
              ((((decoded[1] as u16) << 4) | decoded[0] as u16) as f64
                  * 3.3 / 4095.0 - 1.5) * (1.0 / 0.09);
          src_index += PACKET_SIZE;
          dst_index += 1;
      }
  }
  ...
\end{minted}
\setstretch{2}

The full USB Manager code is provided in Appendix \ref{appendix:software-usb_manager}.

\subsubsection{The Controller} \label{sec:soft-controller}
The Controller thread copies samples from the USB Buffers to the App Buffers.
If enabled by the user, it also performs rising edge triggering and/or frequency
spectrum analysis on the samples. The triggering algorithm uses hysteresis to
find the first rising edge while ignoring rising edges from noise. It does this
by setting the hysteresis to 25\% of the signal peak-to-peak so that only larger
rising edges are triggered on \cite{hysteresis}. Triggering is done on both the
voltage and current channels with separate thresholds provided by the user.
The triggering function is provided below.

\setstretch{1}
\begin{minted}{rust}
    /// Returns position of first rising edge based on threshold
    fn hysteresis_trigger(src: &[f64], trigger: f64) -> usize {
        // Hysteresis width as fraction of peak to peak
        const HYSTERESIS_WIDTH: f64 = 0.25;
        let mut max_val = f64::MIN;
        let mut min_val = f64::MAX;
        for &val in src.iter() {
            max_val = f64::max(max_val, val);
            min_val = f64::min(min_val, val);
        }
        let hysteresis = (max_val - min_val) * HYSTERESIS_WIDTH;

        // Trigger when signal first falls below 'trigger - hysteresis'
        // and then rises above trigger
        let first_lower = src.iter().position(|&val| val < trigger -
            hysteresis);
        if let Some(lower_idx) = first_lower {
            let first_higher = src[lower_idx..].iter().position(
                |&val| val >= trigger);
            if let Some(higher_idx) = first_higher {
                return lower_idx + higher_idx;
            }
        }
        // Don't trigger if it failed
        0
    }
\end{minted}
\setstretch{2}

Spectrum analysis is performed using the \code{spectrum-analyzer} library. The
provided function takes the sample data, sample rate, desired frequency range,
and an optional scaling function and returns a \code{FrequencySpectrum} struct.
This struct contains an array of frequency/magnitude tuples, which can be passed
to the App to be displayed.

The full Controller code is provided in Appendix \ref{appendix:software-controller}
and includes the trigger and spectrum analysis procedures.

\subsubsection{The App}
\code{egui} is a simple and fast GUI library written entirely in Rust \cite{egui}.
It is an immediate mode GUI, which means that the UI is refreshed at approximately
sixty frames per second and does not require any event handlers. This makes it
ideal for writing simple and highly interactive UIs quickly as it eliminates the
need for complex callbacks, UI objects, or state storage. \code{egui} was chosen to
implement the front end for TeachEE instead of JavaScript to avoid the overhead of
message passing.

The function below adds and manages a pair of offset/scale sliders, and is an example
of the simplicity of the \code{egui} library. This function is called three times to
add the three pairs of sliders shown in Figure \ref{fig:soft-ui}.

\setstretch{1}
\begin{minted}{rust}
    fn offset_scale_sliders(
        ui: &mut Ui,
        offset: &mut f64,
        o_range: RangeInclusive<f64>,
        scale: &mut f64,
        s_range: RangeInclusive<f64>,
    ) {
        ui.columns(2, |uis| {
            uis[0].label("Offset");
            uis[0].add(Slider::new(offset, o_range).clamp_to_range(false));
            uis[1].label("Scale");
            uis[1].add(
                Slider::new(scale, s_range)
                    .clamp_to_range(false)
                    .logarithmic(true),
            );
        });
    }
\end{minted}
\setstretch{2}

The App stores two structs: an \code{AppData} and a \code{UIControls}.
\code{AppData} stores the App Buffers, trigger thresholds, and frequency spectrum
enable, and is shared with the Controller thread. \code{UIControls} stores the
current UI state set by the user, e.g., offsets, scaling, trigger thresholds, and
spectrum analysis enable/disable.

TeachEE implements several features reflected in the UI, including:
\begin{enumerate}
  \item Individual channel scaling and offsetting (both horizontal and vertical)
  \item Rising edge triggering with user-provided thresholds
  \item Signal plotting with cursor and various navigation options
  \item Plotting of signals in the frequency domain
  \item Exporting plotted signals to a CSV file
  \item Ability to turn individual channels on and off
\end{enumerate} 
Figure \ref{fig:soft-ui} shows all of TeachEE's features in use at the same time.

\begin{figure}[H]
  \centering
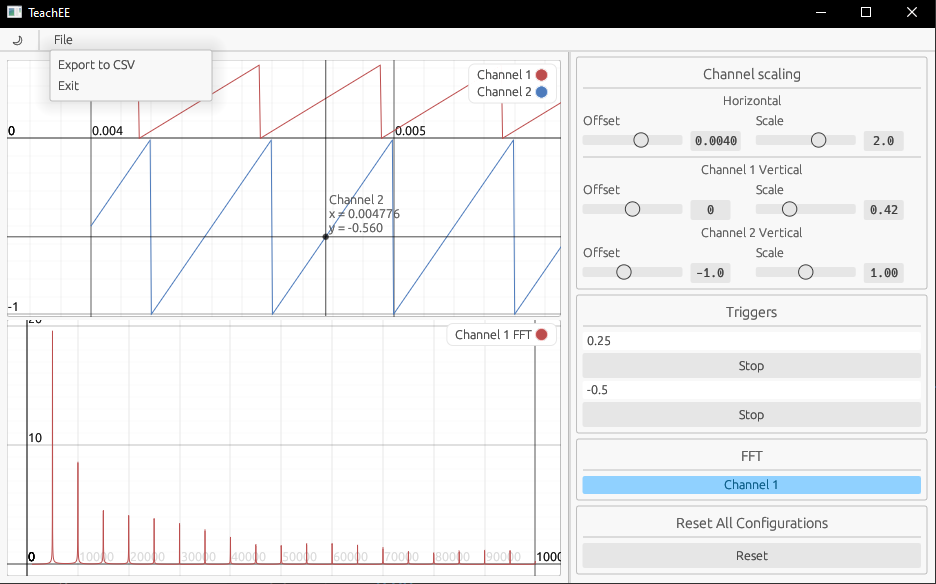
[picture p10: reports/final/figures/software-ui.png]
  
  \caption{Example screenshot showcasing all UI features}
  \label{fig:soft-ui}
\end{figure}

The full App code is provided in Appendix \ref{appendix:software-app} and contains
the UI implementation.

\section{Testing, Evaluation \& Verification} \label{sec:testing}
The testing and validation of TeachEE consisted of testing the hardware/PCB,
FPGA, and software subsystems. The following subsections cover each subsystem of
TeachEE in full detail. Testing was performed in an iterative manner for all
subsystems: a design component was tested in both isolation and integration after being
implemented to ensure that it was implemented and integrated correctly.

\subsection{PCB Verification} % ETHAN
% Hardware tests
The PCB verification process was broken up into physical inspection of the board
and functional testing. The PCBs were both fabricated and assembled by an
external vendor. Upon receiving the fully assembled TeachEE units, the following
physical inspection steps were taken.

\subsubsection{Physical Inspection and Acceptance Testing}
\begin{enumerate}
  \item Microscope examination of the PCB. Looking at each solder joint to
    identify any cold or weak links, tombstoning etc.
  \item Assembly BOM check. Examine the components populated on the board.
    Ensure nothing was missed and make sure that components that were not
    supposed to be populated are left blank, as per the instructions to the vendor.
  \item Solder the linear voltage regulator in for power on testing. This was not
    populated initially because it is through-hole. Through-hole components
    are expensive to assemble so they were done by hand for this project.
  \item Basic electrical check. Use a DMM to check for any short circuits
    between the power rails and ground.
  \item Power on TeachEE via the USB Mini port. Verify that all LEDs
    turn on and that the voltage regulator is outputting the correct voltage.
    Check for heat around the board indicating a possible short circuit.
\end{enumerate}

Figures \ref{fig:pcb-front} and \ref{fig:pcb-back} are the front and back of the
PCB respectively. These photos were provided by the vendor and provide a clear
picture of the boards at the point of delivery and inspection. Figure
\ref{fig:area-around-fifo} is a closeup of the area around the USB FIFO as this
was a high density area in the PCB layout.

\begin{figure}[H]
  \centering
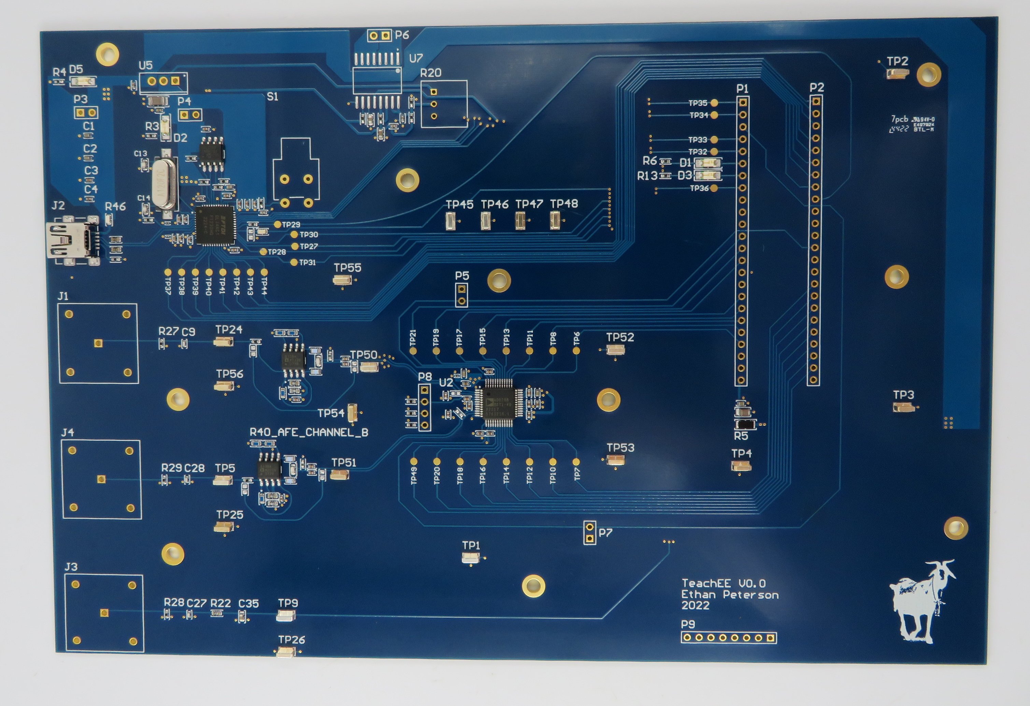
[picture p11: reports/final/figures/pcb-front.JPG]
  
  \caption{PCB Front Side After Delivery}
  \label{fig:pcb-front}
\end{figure}

\begin{figure}[H]
  \centering
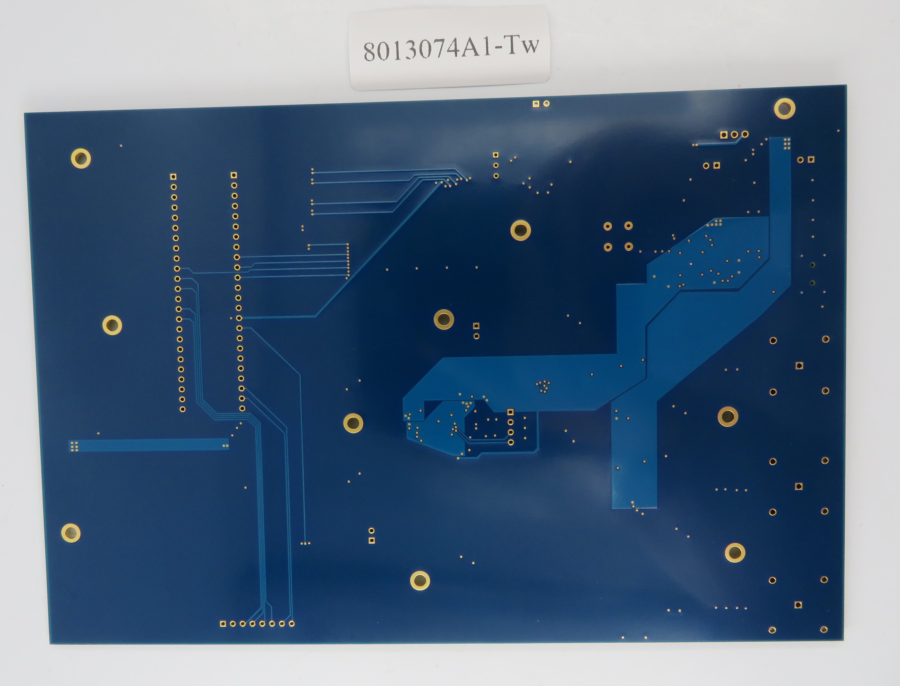
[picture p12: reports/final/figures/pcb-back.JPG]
  
  \caption{PCB Back Side After Delivery}
  \label{fig:pcb-back}
\end{figure}

\begin{figure}[H]
  \centering
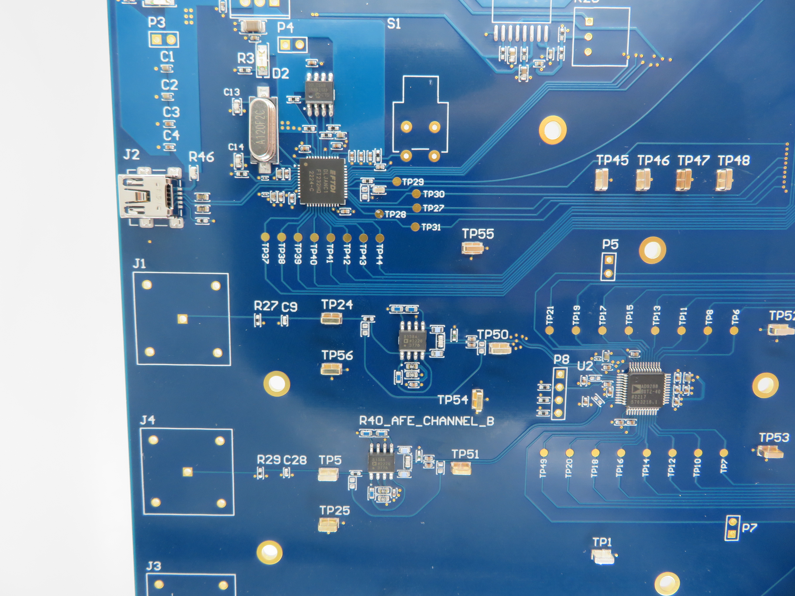
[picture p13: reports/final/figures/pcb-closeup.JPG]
  
  \caption{Close up of the FIFO on the PCB}
  \label{fig:area-around-fifo}
\end{figure}

\subsubsection{Functional Testing}
All three assembled PCBs passed these inspection checks. Next, functional
testing was done on the three units. The functional tests are as follows.

\begin{enumerate}
  \item Plug TeachEE to a computer via the USB Mini connector. Open the FTDI
    Utility to check if the USB FIFO is detected. Ensure that the EEPROM can be
    read and that the USB device descriptor can be changed to \code{TeachEE}.
    After making the EEPROM change, unplug the device and plug back in. Check
    that the USB device is detected with the right descriptor information. This
    descriptor is used by the desktop software to identify the USB device as the
    oscilloscope.
  \item Use the \code{reader.py} script found in Appendix
    \ref{appendix:python-reader} to set the FT232HQ on TeachEE to synchronous
    data transmission mode 40.
  \item After setting the device to synchronous mode, connect an oscilloscope to
    the FT232HQ clock test point on the PCB. Verify that a \SI{60}{\mega\hertz}
    clock is supplied to the FPGA. The waveform should be a triangle wave. A
    screen capture of the clock waveform is given in Figure \ref{fig:ftdi-clk}.
    The triangle wave is not ideal but the FPGA locks to it successfully
    nonetheless.

  % \item Check the output voltage of the hall effect current sensor by probing
  %   the \code{VIOUT} pin with a DMM. This voltage should be approximately
  %   \SI{1.7}{\volt}, which represents a reading of \SI{0}{\ampere}.
\end{enumerate}

% TODO: add figure of the FTDI232HQ clock output
\begin{figure}[H]
  \centering
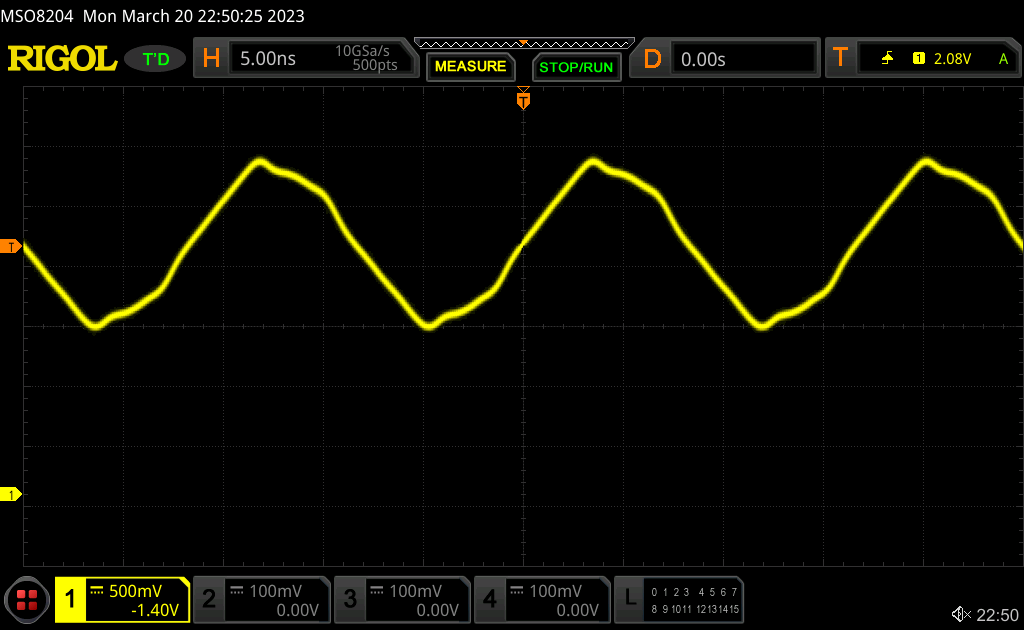
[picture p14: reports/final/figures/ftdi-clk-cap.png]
  
  \caption{FT232HQ Clock Output Waveform}
  \label{fig:ftdi-clk}
\end{figure}

% write a little blurb about doing final assembly
All three PCBs passed the functional tests enumerated above. At this point, all
parts omitted from the assembly process were soldered onto the PCB. This included
all through-hole components on the board except for the voltage regulator, which
was soldered earlier for the power-up test. Through-hole parts were omitted
from the assembly order to keep costs low. Moreover, due to the chip shortage,
the hall effect current sensor had to be purchased separately and soldered
manually. The through-hole parts that were soldered manually included all the pin
headers for the FPGA, BNC connectors for the oscilloscope probes, and
through-hole test points. To protect the PCB from any conductive surfaces or ESD,
M3 standoff screws were installed into all the mounting holes. After this
final assembly step, the PCB was ready for software and FPGA development. The
FPGA module can be installed into the pin header and flashed. A fully assembled
TeachEE is shown in Figure
\ref{fig:pcb-final}.

\begin{figure}[H]
  \centering
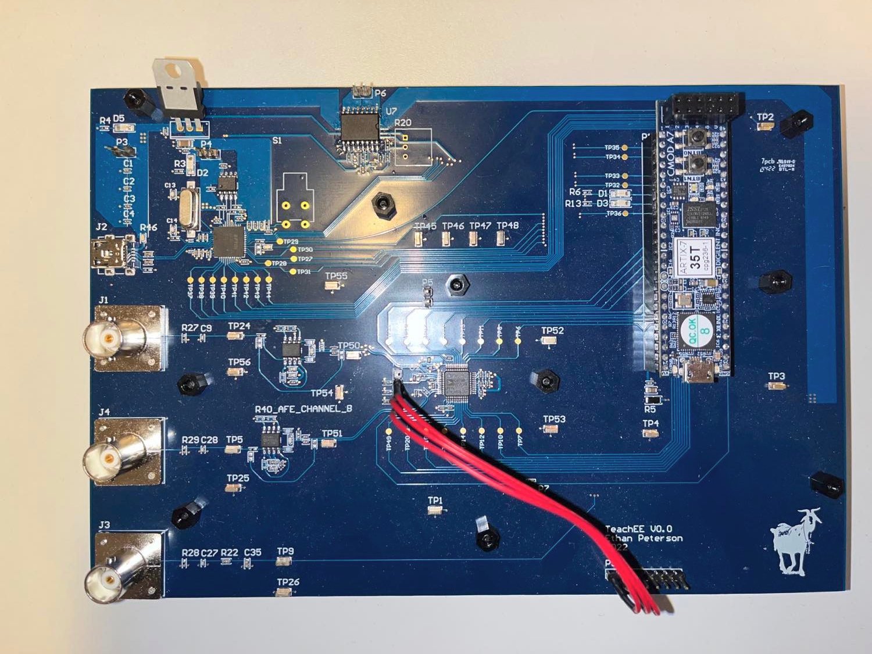
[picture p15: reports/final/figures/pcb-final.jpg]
  
  \caption{Final Assembled TeachEE}
  \label{fig:pcb-final}
\end{figure}

\subsection{FPGA Verification} % ETHAN

% Talk about FPGA automated sims, testbenches CI ETC

FPGA code testing was a continuous process taking place throughout the
development cycle. SystemVerilog modules are tested and verified using
``testbenches''. Testbenches are modules that wrap around the module to be
tested and modulate the input signals through a variety of test cases
designed by the programmer. Example testbenches can be found in Appendix
\ref{appendix:rtl-leg-tb} and \ref{appendix:rtl-vunit-tb} respectively.

The verification of the code takes place on a per-module basis using one
testbench per module. This includes complex modules such as the packetizer, but
also simple modules that wrap AXIS interfaces. This allows each module to be
evaluated and verified independently of one another, ensuring easy integration
into the broader TeachEE codebase.

Initially, testbenches were made up of a finite state machine that applied
different inputs to the module, with the outputs being manually inspected by the
developer in ModelSim. These initial testbenches are shown in
Appendix \ref{appendix:rtl-leg-tb}. As the FPGA development process continued,
it quickly became difficult to manually inspect simulation waveforms due to the
large number of outputs and multi-cycle operations. An example of
one of the larger waveforms that needed to be manually inspected is shown in
Figure \ref{fig:xadc-packetizer-modelsim}.

\begin{figure}[H]
  \centering
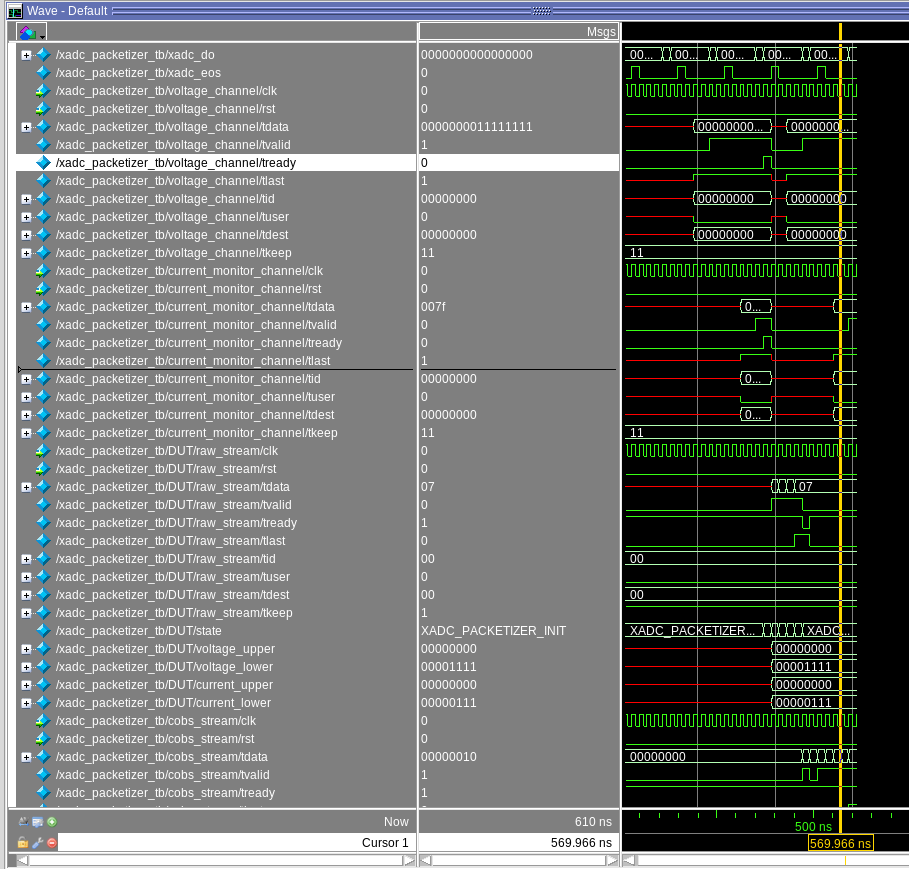
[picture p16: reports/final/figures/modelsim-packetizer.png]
  
  \caption{Example ModelSim Waveform from a Packetizer Module}
  \label{fig:xadc-packetizer-modelsim}
\end{figure}

\subsubsection{Verification Automation With VUnit}
To speed up testbench development and debugging, an automated testing
framework, VUnit, was introduced. VUnit provides macros within SystemVerilog
to make assertions on the values of registers and wires \cite{vunit}. An example of
a SystemVerilog testbench written for use with VUnit is given in Appendix
\ref{appendix:rtl-vunit-tb}. This greatly improved development speed as checks
were automated and manual inspection was no longer required, except for specific
debugging tasks. Moreover, VUnit also allows testbenches to be specified in a
Python script. These Python scripts specify the dependencies and source files
needed to run the test as well. To run a testbench, it is as simple as running
the corresponding Python script so long as the simulation tool (ModelSim) and
VUnit package is installed. Each VUnit testbench has an accompanying Python file. A
Python testbench example is provided in Appendix \ref{appendix:python-vunit-tb}.

Another significant benefit of using VUnit is that it makes the testbenches
easily callable from a command line interface (CLI). In order to further
automate the testing, Continuous Integration (CI) was added to the TeachEE code
repository. The TeachEE code is hosted in a GitHub repository
\cite{teachee-github}. GitHub provides a tool called Actions which can be used
to run automated scripts on new code changes introduced to the repository in
pull requests \cite{github-actions-doc}. Since the VUnit testbenches are easily
callable from a script, a GitHub Actions script was introduced to run all the
testbenches on each pull request. The full source code is provided in Appendix
\ref{appendix:github-action-script}. The script installs ModelSim and Vunit, then
runs the testbenches, reporting any errors automatically when new code is pushed.
This ensured that new code did not break compatibility with older modules.

\subsubsection{Hardware Simulation with BFMs}
In many cases, additional supporting modules were needed to test a specific
module. Examples of this are the \code{ft232h}, \code{xadc_drp_axis_adapter},
and \code{hsadc_axis_adapter}. Since all of these modules were designed to
interact with the interface of a physical component on the PCB, mock interfaces
were needed to test the module. These device mocks are called
``Board Functional Models'' or BFMs. Each BFM is designed to respond in the same
way to input as the actual device itself. Of course, the BFM has no real data to
return so the data coming back will often be a preset value or known pattern.
The BFMs are written as finite state machines built to emulate the timing
diagrams provided by the manufacturer for a specific part. Usually, they are
more limited in their scope compared to the full device interface to limit the
potential for bugs. For example, \code{ft232h_bfm} only implements the write
interface of the FT232HQ as the USB reads are not used in TeachEE. The main
problem with BFMs is that they can produce bugs of their own. However, if the
BFM is correct, then a module interacting with the hardware modeled by the BFM
should work exactly as expected on the physical PCB. An example BFM that mocks
the interface of the XADC is given in Appendix \ref{xadc-bfm}.

\subsubsection{FPGA Bugs and Solutions} \label{sec:fpga-bugs}
During the FPGA and hardware verification process, the most difficult bugs were
at the intersection of the PCB hardware and FPGA. Specifically, bringing up the
FT232HQ and transmitting data proved difficult. The main reason for this is
that without the USB FIFO up and running, there is little visibility into the
FPGA firmware beyond the on-status LEDs and JTAG debugger. As a result, it was
extraordinarily difficult to distinguish whether an issue was hardware or FPGA
related. Eventually, it was discovered that an error in the state machine caused
the \code{ft232h} module to start sending data before the chip was ready to
accept it, leading to lost bytes or no bytes at all. After resolving this
misunderstanding of the device interface, it was discovered that the data was
being received but bytes were still missing. After probing the test points on the
USB FIFO using an external oscilloscope, it was discovered that data is sent for
one extra cycle after the USB FIFO stops accepting data, leading to dropped
bytes. This was not a misunderstanding of the device function, but rather a
misuse of asynchronous assignments in the code.

After resolving the dropped bytes and building a reliable channel, testing the
remaining modules in hardware was far simpler as the output of such modules
could be fed directly to the connected computer and evaluated.

Aside from Data Integrity, power-on race conditions proved an issue for the
FPGA design. Since the design is dependent on an external clock generated by the
USB FIFO, the data transmission often did not start up
correctly if the clock was not received in a timely manner during the boot
sequence. The clock was not available immediately since the device first had be
set to synchronous mode by the software to produce the clock. This issue was
resolved by probing the clock output pin of the FT232HQ during start-up and
triggering on the first clock edge. Once the source of the problem was
established, a clever use of the \code{locked} output of the PLL was used to hold
all modules in reset until the clock becomes available.

\subsection{Software Verification} \label{sec:software-verification} % ERIC
% Rust CI, Testing with mock byte streams? 
% Threading model iteration, trigger iteration
% Testing decoding algo with recorded bytestream and asserts (adding error handling)
% FFT testing (using lab sig gen, discovered incorrect sample rate)
Overall software validation was done throughout the development life cycle using
two tools. The first tool was a mock bytestream generator that populates the channel
buffers with sawtooth waves. The generator simulates data arriving from the hardware
and allowed developers to test Controller and App functionality without TeachEE
hardware. This greatly increased development flexibility as the developers could
write code and immediately test it remotely. For example, the trigger functionality
correctness was verified with these mock bytestreams rather than the hardware. The mock
bytestream code is provided in Appendix \ref{appendix:software-sine}. The
second tool was an automated GitHub Action script run on every branch that builds the
software, checks code formatting, and runs a linter to catch common mistakes. This
tool ensured that code merged to the main branch was written with good style and did
not introduce any build errors. This script is provided in Appendix
\ref{appendix:software-script}.

\subsubsection{Design Iteration} \label{sec:soft-performance-issues}
Severe performance issues were encountered while implementing the initial
software design described in Section \ref{sec:soft-design}. The frame rate of the
UI was limited to approximately ten frames per second. This issue was caused by high
levels of mutex contention: the USB Manager thread would repeatedly acquire the
mutex, thereby starving the App thread.
Because threads did not take turns, they could overwrite new data or read stale
data. The new implementation addressed these concerns by using monitors to
prevent redundant read/writes and limit contention, and runs at an average of fifty
frames per second. These frame rates were measured using instrumentation code run
in the UI update function. The code is provided below.

\setstretch{1}
\begin{minted}{rust}
  ...
  self.counter += 1;
  if self.start.elapsed() > Duration::from_secs(1) {
      println!("{}", self.counter);
      self.counter = 0;
      self.start = Instant::now();
  }
  ...
\end{minted}
\setstretch{2}

The triggering functionality also underwent design iteration. The initial
triggering algorithm used a moving average sliding window as the noise
mitigation strategy. It required that the average of the last \code{WINDOW_SIZE}
samples be less than the currently analyzed sample, in addition to requiring that the
currently analyzed sample be greater than the trigger threshold. The sliding window
iterator is shown below.

\setstretch{1}
\begin{minted}{rust}
  const WINDOW_SIZE: usize = 10;
  let mut sum: f64 = src[lower_idx..(lower_idx + WINDOW_SIZE)].iter().sum();
  // Iterate over all windows of size WINDOW_SIZE + 1. The first WINDOW_SIZE
  // samples are used to calculate the average value of previous samples,
  // which is then compared to the last sample. This is done to find a
  // rising edge while attempting to filter out noise.
  let first_higher = src[lower_idx..]
      .windows(WINDOW_SIZE + 1)
      .position(|window| {
          let val = *window.last().unwrap();
          val >= trigger && sum / (WINDOW_SIZE as f64) < val || {
              // Update sliding window.
              sum += val;
              sum -= *window.first().unwrap();
              false
          }
      });
\end{minted}
\setstretch{2}

Although this algorithm functioned well, it produced slightly unstable
waveforms and did not consistently trigger at the exact same position on every
iteration of a signal. Furthermore, concerns were made about the validity of
the algorithm and the team wanted a more conventional implementation. These issues
led to the research and implementation of the current hysteresis-based triggering
algorithm described in Section \ref{sec:soft-controller}.

\subsubsection{Feature Testing}
Every implemented feature was rigorously tested before proceeding with new features.
For example, the packet decoding functionality was tested using bytestreams
redirected from the hardware to a file. Because the voltage and current values
from the file were known, they could be compared to the voltage and current values
after being decoded by the software algorithm. This verified that the packets
were being decoded correctly and that the bytes were mapped to the right
voltage/current values. Additionally, assertions were used to alert the team
of any unexpected packet errors. These assertions led to the discovery of the
packet encoding problem described in Section \ref{sec:fpga-bugs}. They also
prompted additional decoder error handling as the bytestream channel was found
to not be completely reliable.

Software bugs were also discovered during testing of the frequency spectrum
analysis feature. The library provided spectrum analysis function produced
frequencies twice that of signals generated using a lab signal generator.
This factor-of-two error was ultimately determined to be caused by an
incorrect sample rate assumption in software. Although the hardware was
indeed sampling at \SI{1}{\mega\samplepersec}, the sample rate per channel
with two channels was actually \SI{500}{\kilo\samplepersec}. This correction
fixed both the FFT functionality and the plots' time scales.

\section{Project Planning and Budgeting} % ERIC

The following table lists the original milestones associated with this project.
\begin{table}[H]
    \caption{Milestones}
    \begin{tabularx}{\textwidth}{l|l|l|l}
        No. & Milestone & Due date & Responsible Member(s) \\
        \hline
        1 & Design and order PCB & Week 4 & Ethan \\
        2 & Create skeleton of application & Week 11 & Tim \\
        3 & Submit blueprint report & Week 11 & All members \\
        4 & Verify PCB is functional & Week 12 & Ethan \\
        5 & Read values from USB driver & Week 13 & Tim and John \\
        6 & Create basic UI and waveform display & Week 14 & Eric \\
        7 & FPGA programming & Week 16 & Ethan \\
        8 & Implement oscilloscope triggering & Week 16 & John \\
        9 & Implement CSV exporting and all UI functionality & Week 17 & Eric \\
        10 & Testing of application & Week 18 & Tim, Eric, and John \\
        11 & Testing of PCB & Week 18 & Ethan \\
        12 & Testing of complete system & Week 20 & All members \\
        13 & Open House & Week 22 & \\
        14 & Final deliverable & Week 23 & \\
        15 & Final project report & Week 24 & All members
    \end{tabularx} 
\label{hw:milestones-table}
\end{table}

Many milestones were completed earlier than planned; in particular, the full FPGA
and UI work were completed between weeks 12 and 13, and basic triggering was
implemented in week 15. Due to the severe software performance issues described in
Section \ref{sec:soft-performance-issues}, developing a new design became the top priority.
This slightly delayed some less important UI work, but all required functionality was
completed by week 19. Furthermore, many stretch goals were achieved, including
reading from four concurrent channels, advanced triggering, and frequency spectrum
analysis. Also, minimal testing was required near the end of the timeline as most
issues were solved during development through iterative testing.

Table \ref{tab:abbreviated-bom} breaks down the cost of the PCB
fabrication and assembly as quoted by the supplier. The supplier contracted for
TeachEE is Bittele (7PCB). Bittele takes care of both the fabrication and
soldering of the PCBs. Moreover, Bittele takes the generated output from the EDA
software (Altium) and procures all the parts directly to their facility. The
procurement cost is expanded in the budget table with the major functional
components on the PCB. An exhaustive list is not included as there are hundreds
of miscellaneous resistors, capacitors, and inductors with marginal cost.

A full unit of the PCB cost \$80 less than the target budget. This left
additional budget to purchase replacement components and
cover unexpected expenses. Two additional backup boards were ordered in case the main
board failed. Fortunately, the team did not encounter any hardware failures during the
course of the project and therefore did not require any replacing of the board or its
components. The full BOM for the PCB is provided in Appendix \ref{appendix:bom}.

\begin{table}[H]
    \caption{TeachEE Bill of Materials}
    \begin{tabularx}{\textwidth}{l|l|l}
        \textbf{Item / Part Number} & \textbf{Supplier} & \textbf{Cost (CAD)} \\
        \hline
        PCB Fabrication & Bittele & \$104.37\\
        PCB Total BOM Procurement & Bittele & \$126.67\\
        \hline
        \textbf{Major Components (Included in cost above)}& &\\
        \hline
        AD9288BSTZ-40 ADC & Digi-Key & \$14.70\\
        AD8138ARZ-R7 ADC Driver & Digi-Key & \$26.85\\
        FT232HQ-REEL USB FIFO & Digi-Key & \$6.41\\
        ACS720KLATR-15AB-T Current Sensor & Digi-Key & \$9.81\\
        \hline
        PCB Assembly & Bittele & \$289.76\\
        \hline
        Total & & \$520.80\\
        \hline
        Budget Remaining & & \$79.20
    \end{tabularx} 
\label{tab:abbreviated-bom}
\end{table}

\section{Stakeholder Needs} \label{sec:stakeholder-needs} % John / Tim
%% Describe how you considered stakeholder needs in your design, and how factors
%% like safety, privacy, codes/standards, manufacturability, ethics and cost were
%% considered in your design.

% JOHN should use this section to discuss why our device is more suited to EE
% undergrads than what is currently on the market. Tim should provide some input
% on manufacturability and cost too.

% Add something about how an EE professor and stakeholder (Whitehall) noted that
% the scopes provided in his class's lab kits didn't have a good FFT implementation
% (difficult to tell whether the screen showed time domain or FFT, could not
% simultaneously display both time and frequency plots) so we took his needs into
% account with our implementation (which clearly shows time or FFT and both at the
% same time)

\subsubsection{Features and Quality}

%% Ethan, if you could elaborate on why the kits were bad that would be great.
%% John finds it difficult to comment since he did not use the kits
%% Emphasis on the "quality" point

%% and to double check, we did indeed have scroll to zoom functionality?

In the online electrical engineering labs during the pandemic, an electronics
professor noticed issues with the kits provided to students. There was a general
lack of quality and brittleness which caused students to require replacement
kits. Additionally, the oscilloscopes and signal generators had few protections
against extraneous inputs, resulting in students accidentally breaking their
tools when incorrectly connected. At a functional level, the oscilloscopes were
missing critical features: they were single channel and had no ability to
measure current or perform frequency domain analysis.

Beyond the lab kits, the archaic design of a typical oscilloscope can be
improved upon. Rather than rotating physical knobs to adjust the display, it is
more intuitive to interact with the application like you would any other:
through the interface of a computer application. This benefits novice engineers
that are unfamiliar with traditional oscilloscopes' interfaces.

TeachEE addresses these stakeholder needs. The
application is intuitive to use, with the ability to click and drag to adjust
the waveform display, as well zooming via mouse scroll. It can also
intuitively display the spatial and time domain of signals at the same time.

\subsubsection{Safety}

As was mentioned in Section \ref{sec:software-verification}, the software has been
thoroughly tested to ensure stability for users. In particular, the choice of
Rust in the presence of complex threading models yields a high degree of
confidence that undefined behaviour is avoided. Given that TeachEE can export
CSV files onto the host computer, this opens a vector of damage. If these
precautions were not taken then there is the possibility that TeachEE enters an
invalid state and writes to the user's computer in an undesirable way.

A computer can be damaged through the USB port by devices such as ``USB Killers''
\cite{usb-killer}. Since TeachEE works with high voltage and current, it is
important to ensure protection of the user's computer during operation. The
computer is protected from backflow by diodes in the voltage regulator.
Additionally, on the device itself, the AFE clamps voltages that
are too high.

\subsubsection{Manufacturing Cost}

The viability of manufacturing TeachEE at scale is promising due to the current
design's significant drop in unit cost at increased volume.  At scales greater
than 100 units, the team estimates that the cost-per-unit could drop as low as
\$250. This reduction in cost provides an opportunity for competitive pricing
compared to the PicoScope\textregistered~4000, a USB oscilloscope with similar
specifications to TeachEE. The manufacturers' price for a
PicoScope\textregistered~4000 starts at \$930, indicating a potential profit of
up to 272\% if the TeachEE were sold at scale for \$930 per unit
\cite{picoscope}. These figures suggest that TeachEE could be a viable product
with the potential for a good return on investment.

\section{Compliance with System Requirements} % John
%% Compliance with specifications – Include your original specifications table from
%% the Blueprint and add extra column to it as shown below and report what you
%% obtained with your final design. If any of your specs were not achieved or fell
%% outside the tolerance values, explain why in this section. Your mark for this
%% section depends on how close you got to your specs

% NOTE: John please finish off this section, i just did the tables, - ethan
The following tables outline the target hardware and software specifications of
this project. The hardware and software specification evaluations are given in
Tables \ref{tab:hw-spec-eval} and \ref{tab:sw-spec-eval} below, and show that
the prototype meets or exceeds the specifications in all areas.

\begin{table}[H]
    \caption{Hardware Specification Evaluation}
    \begin{tabularx}{\textwidth}{c|c|c|p{5cm}}
        Specification & Target Value & Achieved? & Comments \\
        \hline
      Voltage Input Bandwidth&\SI{100}{\kilo\hertz}& Yes & Ultimately \SI{500}{\kilo\hertz} of bandwidth was achieved through the low speed ADC and \SI{20}{\mega\hertz} through the high speed ADC.\\
        \hline
        Current Input Bandwidth&\SI{100}{\kilo\hertz}& Yes & This bandwidth matches the hall effect sensor.\\
        \hline 
        Measurable Current Range&\SI{-15}{\ampere} to \SI{+15}{\ampere}& Yes & Matches the specification of the sensor.\\
        \hline
        Measurable Voltage Range& \SI{0}{\volt} to \SI{3.3}{\volt} & Yes & This was achieved in both XADC and HSADC channels.\\
        \hline
        Number of Current Input Channels& $1$ & Yes & \\
        \hline
        Number of Voltage Input Channels& $1$ & Yes & Two additional voltage channels were added using the HSADC.\\
        \hline
        Power Input Voltage Rating& \SI{5}{\volt} & Yes & USB voltage is used as supply and the regulator is tolerant up to \SI{12}{\volt}.\\
        \hline
        Power Current Consumption Rating& \SI{500}{\milli\ampere} & Yes & Current draw has not exceeded \SI{500}{\milli\ampere} in any operation setting.\\
        \hline
        Voltage Sample Rate& \SI{1}{\mega\samplepersec} & Yes & The XADC can sample at \SI{1}{\mega\samplepersec} and HSADC can sample at \SI{40}{\mega\samplepersec}.\\
        \hline
        Current Sample Rate& \SI{1}{\mega\samplepersec} & Yes & \\
        \hline
        PCB Thickness& \SI{1.6}{\milli\metre} & Yes & Thickness was exactly 1.6 mm in a four-layer stackup. \\
        \hline
        PCB Dimensions& $\pm \SI{400}{\milli\metre\squared}$ & Yes & The tolerance given is less than the final size of the PCB.\\
        \hline
        Voltage Sample Error & $\pm \SI{20}{\percent}$ & Yes & Values match almost exactly to the Rigol scope in the Sci '65 lab through empirical testing.\\
        \hline
        Current Sample Error & $\pm \SI{20}{\percent}$ & Yes & Current readings match a DMM within this tolerance.\\
        \hline
    \end{tabularx} 
\label{tab:hw-spec-eval}
\end{table}

\begin{table}[H]
  \caption{Software Specification Evaluation}
  \begin{tabularx}{\textwidth}{p{8cm}|l|p{6cm}}
    Specification & Achieved? & Comments\\
    \hline
    The software shall be able to modify the horizontal and vertical scales of the plot. & Yes & Multiple plot navigation methods, including touch screen and trackpad compatibility. \\
    The software shall be able to modify the trigger voltage. & Yes & Triggering algorithm was exceptionally stable. \\
    The application shall be deployable to Windows, macOS, and Linux. & Yes & \\
    \hline
    The software shall be able to capture voltage samples and export them to a CSV file. & Yes & \\
    The software shall receive samples via the FTDI 232 in synchronous mode. & Yes & \\
    \hline
    The software shall be able to render waveforms at a rate of \SI{30}{\hertz} on screen. & Yes & Achieved \SI{50}{\hertz} with final design. \\
    \hline
  \end{tabularx} 
  \label{tab:sw-spec-eval}
\end{table}

\section{Conclusions \& Recommendations} % Tim
%% Conclusions and recommendations – provide commentary on the main technical
%% lessons learned from this project; is there potential for lasting impact for
%% this project beyond this course? Can more research be done in an area? Should
%% someone tackle this problem again but using a different approach? Is there
%% potential for commercialization? If this were to be scaled out to a commercial
%% version how would it be manufactured and what would the cost be? Speculate about
%% the market size for such a product. If the product makes it to the market, what
%% are the potential positive and adverse societal and cultural impacts of the
%% product? How can the adverse impacts be mitigated?
% See open house poster for inspiration

Developing TeachEE provided the team with several valuable technical lessons,
including the value of using Rust for applications requiring high performance
and concurrency. Rust's focus on memory safety and zero-cost abstractions makes
it an ideal choice for building high-performance systems with low-level
control. The team found that Rust enabled them to write code that was both safe
and efficient, allowing them to achieve the necessary performance requirements
for the TeachEE prototype. Overall, the team believes that Rust was a key
factor in the success of the TeachEE project, and they plan to continue using
it for future projects that require high performance and concurrency.

Another key lesson learned is to avoid assuming ideal specifications for hardware
components, for example, assuming ideal speeds for USB 2, which were not
achievable in practice. Such assumptions led to unexpected issues in the
prototype. As a result, adjustments needed to be made to accommodate the actual
capabilities of the components. This experience taught the team the importance
of conducting thorough research on the specifications of hardware components
and testing them under realistic conditions.

In conclusion, the team considers the TeachEE prototype to be a success
and are proud to have met or exceeded all the product requirements.
If TeachEE were to be launched as a product, it could 
potentially create lasting impact on the field of engineering by reducing the
barrier of entry for aspiring electrical engineers. TeachEE's low cost makes it
more accessible to students and hobbyists who may not have access to expensive
laboratory equipment (see Section \ref{sec:stakeholder-needs}). By providing an
affordable tool for learning and experimentation, TeachEE can help to
democratize access to electrical engineering education and enable a more diverse
range of individuals to engage with the discipline. For these reasons, the team
believes further development in products like TeachEE is worthwhile.

\section{Overall Team Effort}
The following table quantifies the percentage effort each team member expended
on all aspects of the project.

% NOTE: I think we will need to add some further reflection here about how the
% project went overall, it is in the rubric
\begin{table}[H]
  \caption{Team Effort Table}
  \centering
  \begin{tabularx}{10cm}{l|l}
    \textbf{Name} & \textbf{Effort Expended \%}\\
    \hline
    Ethan Peterson & TODO \\
    \hline
    Eric Yang & TODO \\
    \hline
    Timothy Morland & TODO \\
    \hline
    John Giorshev & TODO \\
  \end{tabularx} 
\end{table}
\newpage

\setstretch{1.4}
\bibliographystyle{IEEEtran}
\bibliography{report}

\newpage
\setstretch{1}
\newcommand{\changelocaltocdepth}[1]{%
  \addtocontents{toc}{\protect\setcounter{tocdepth}{#1}}%
  \setcounter{tocdepth}{#1}%
}
\changelocaltocdepth{1}

\pagestyle{empty}

    \begin{appendices}
        \begin{landscape}
        \section{Schematics}
        \label{appendix:schematic}
    \centering
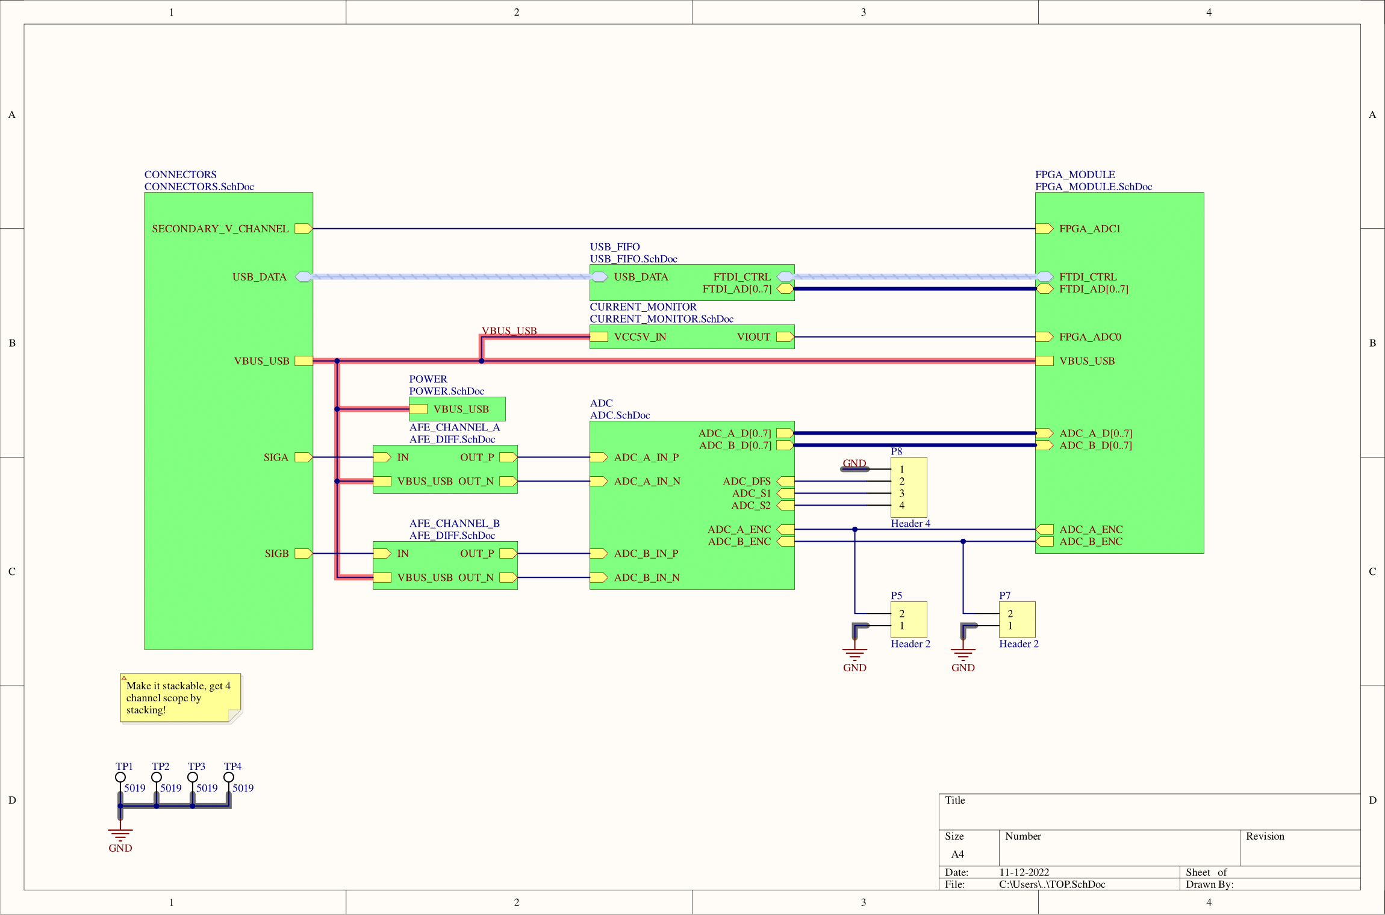
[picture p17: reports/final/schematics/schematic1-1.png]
    
        \end{landscape}
    \includepdf[pages=-,landscape=true]{schematics/schematic2-8.pdf}

        \begin{landscape}
        \section{PCB Layout}
        \label{appendix:layout}
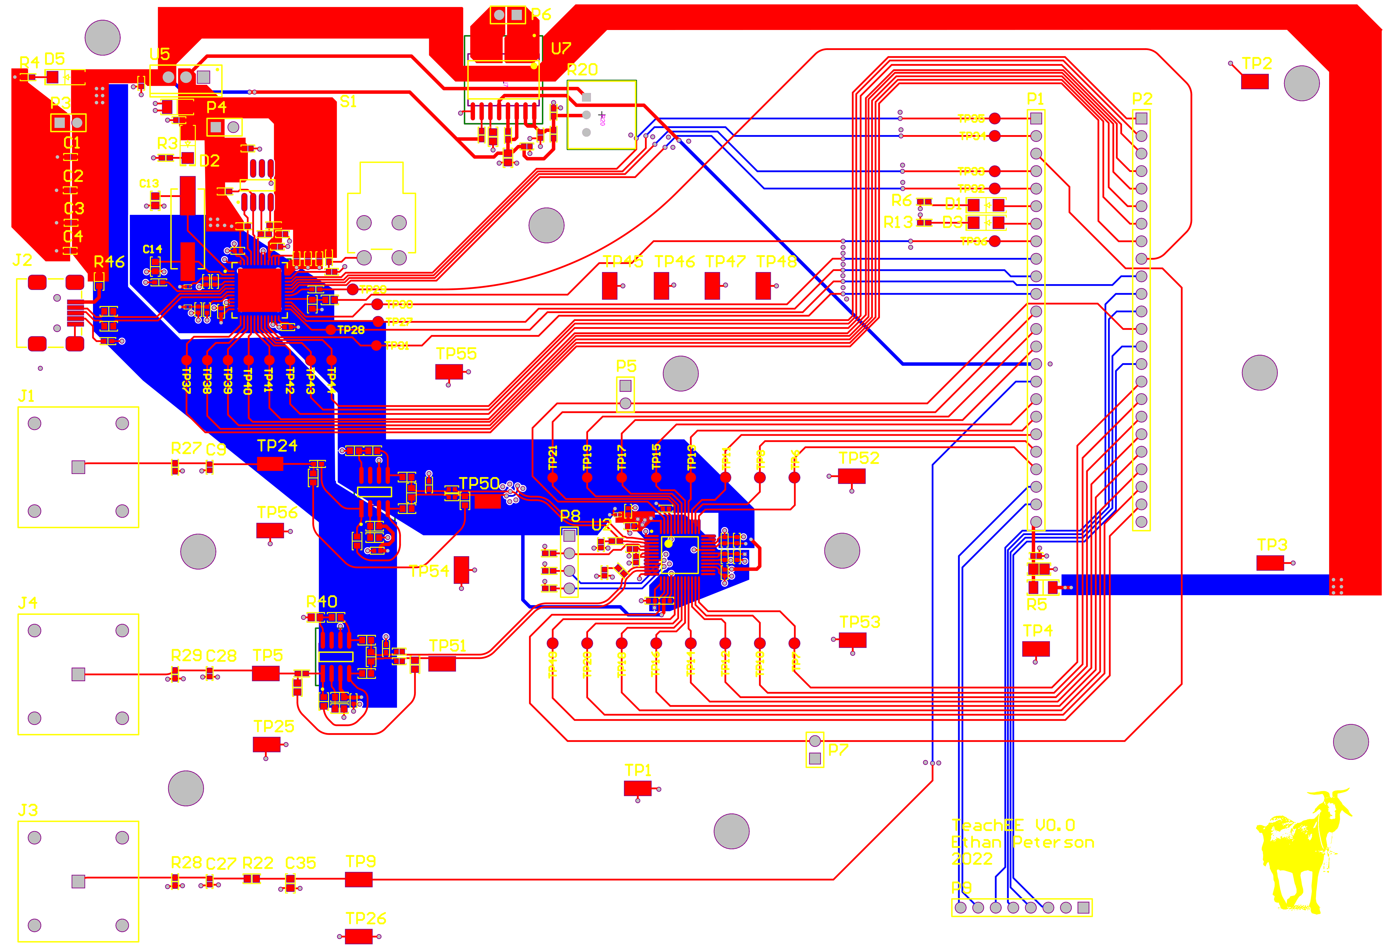
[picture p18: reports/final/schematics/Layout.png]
    
        \end{landscape}

        \section{PCB Bill of Materials}
        \label{appendix:bom}
    \begin{table}[H]
    \begin{tabular}{p{1.7in}|p{0.3in}|p{0.8in}|p{0.7in}|p{0.7in}|p{1in}}
        \textbf{Designator} & \textbf{QTY} & \textbf{Description} & \textbf{Comment} & \textbf{Footprint} & \textbf{Part Number} \\ \hline 
        C1, C2, C37, C48 & 4 & CAP CER 10UF 10V X5R 0402 & 10 µF & CAP 0402\_1005 & CL05A106MP8NUB8 \\ \hline
        C3 & 1 & CAP CER 1UF 10V X7S 0402 & 1 µF & CAP 0402\_1005 & GRM155C71A105KE11D \\ \hline
        C4, C11, C16, C17, C18, C19, C20, C21, C22, C24, C26, C29, C30, C38, C39, C40, C41, C42, C43, C44, C45, C46, C47, C50\_AFE\_CHANNEL\_A, C50\_AFE\_CHANNEL\_B, C52\_AFE\_CHANNEL\_A, C52\_AFE\_CHANNEL\_B, C53\_AFE\_CHANNEL\_A, C53\_AFE\_CHANNEL\_B & 29 & CAP CER 0.1UF 50V X5R 0402 & 0.1 µF & CAP 0402\_1005 & CGA2B3X5R1H104M050BB \\ \hline
        C5, C12, C32, C34 & 4 & CAP CER 0.1UF 10V X7R 0402 & 0.1µF & CAP 0402\_1005 & 0402ZC104KAT2A \\ \hline
        C6 & 1 & CAP CER 10UF 16V X5R 1206 & 10 µF & CAP 1206\_3216 - 0.8MM & EMK316BJ106MD-T \\ \hline
        C7 & 1 & CAP CER 10UF 35V X6S 0805 & 10 µF & CAP 0805\_2012 & GRM21BC8YA106KE11L \\ \hline
        C8, C15, C23, C25 & 4 & CAP CER 4.7UF 16V X5R 0402 & 4.7 µF & CAP 0402\_1005 & CL05A475MO5NUNC \\ \hline
        C9, C27, C28 & 3 & CAP CER 20PF 25V NP0 0402 & 20pF & CAP 0402\_1005 & 04023U200JAT2A \\ \hline
    \end{tabular}
    \end{table}

    \newpage

    \begin{table}[H]
    \begin{tabular}{p{1.7in}|p{0.3in}|p{0.8in}|p{0.7in}|p{0.7in}|p{1in}}
        \textbf{Designator} & \textbf{QTY} & \textbf{Description} & \textbf{Comment} & \textbf{Footprint} & \textbf{Part Number} \\ \hline 
        C10 & 1 & CAP MLCC 0.01UF 100V X7R 0402 & 10000 pF & CAP 0402\_1005 & HMK105B7103KVHFE \\ \hline
        C13, C14 & 2 & CAP CER 36PF 100V NP0 0603 & 36pF & CAP 0603\_1608 & 06031A360JAT2A \\ \hline
        C31 & 1 & CAP CER 1UF 16V X7R 0603 & 1 µF & CAP 0603\_1608 & C0603C105K4RACAUTO \\ \hline
        C33, C35 & 2 & CAP CER 0603 4.7NF 16V X7R 10\% & 4700 pF & CAP 0603\_1608 & C0603C472K4RECAUTO \\ \hline
        C51\_AFE\_CHANNEL\_A, C51\_AFE\_CHANNEL\_B & 2 & CAP CER 15PF 25V C0G/NP0 0603 & 15 pF & CAP 0603\_1608 & C0603C150J3GACAUTO \\ \hline
        D1, D3 & 2 & LED SMD & Blue & LED 1206\_3216 BLUE & APTL3216QBC/D-01 \\ \hline
        D2, D5 & 2 & LED SMD & Green & LED 1206\_3216 GREEN & APTL3216ZGCK-01 \\ \hline
        FB1, FB2, FB3 & 3 & FERRITE BEAD 33 OHM 0201 1LN & 33 Ohms @ 100 MHz & FER 0201\_0603 & MMZ0603F330CT000 \\ \hline
        J1, J3, J4 & 3 & Jack BNC Connector, 1 Position, Height 16.26 mm, Tail Length 6.35 mm, -55 to 85 degC, RoHS, Tube & 5227699-2 & & 5227699-2 \\ \hline
        J2 & 1 & CONN RCPT MINI USB B 5POS SMD RA & & & 10033526-N3212LF \\ \hline
    \end{tabular}
    \end{table}
    \newpage
    \begin{table}[H]
        \begin{tabular}{p{1.7in}|p{0.3in}|p{0.8in}|p{0.7in}|p{0.7in}|p{1in}}
        \textbf{Designator} & \textbf{QTY} & \textbf{Description} & \textbf{Comment} & \textbf{Footprint} & \textbf{Part Number} \\ \hline 
        R1, R2 & 2 & RES SMD 10 OHM 0.1\% 1/10W 0603 & 10 Ohms & RES 0603\_1608 & CRT0603-BY-10R0ELF \\ \hline
        R3, R6, R13 & 3 & RES 220 OHM 1\% 1/8W 0402 & 220 Ohms & RES 0402\_1005 & CRGP0402F220R \\ \hline
        R4 & 1 & RES SMD 330 OHM 5\% 1/16W 0402 & 330 Ohms & RES 0402\_1005 & AC0402JR-07330RL \\ \hline
        R5 & 1 & 1206 40 AMP JUMPER & 0 Ohms & RES 1206\_3216 & JR1206X40E \\ \hline
        R7 & 1 & RES SMD 12K OHM 0.1\% 1/16W 0402 & 12 kOhms & RES 0402\_1005 & CPF0402B12KE1 \\ \hline
        R8, R9, R10, R11, R17, R18, R19, R21, R32, R33, R34 & 11 & RES 10K OHM 0.1\% 1/10W 0402 & 10 kOhms & RES 0402\_1005 & RP73PF1E10KBTD \\ \hline
        R12 & 1 & RES 1.8K OHM 1\% 1/16W 0402 & 1.8 kOhms & RES 0402\_1005 & RC0402FR-071K8L \\ \hline
        R14 & 1 & RES SMD 100K OHM 0.1\% 1/16W 0402 & 100 kOhms & RES 0402\_1005 & CPF0402B100KE \\ \hline
        R15, R46 & 2 & RES SMD 0 OHM JUMPER 1/2W 0603 & 0 Ohms & RES 0603\_1608 & 5110 \\ \hline
        R22 & 1 & RES SMD 75 OHM 1\% 1/10W 0603 & 75 Ohms & RES 0603\_1608 & AC0603FR-0775RL \\ \hline
        R26 & 1 & RES 24 OHM 1\% 1/16W 0402 & 24 Ohms & RES 0402\_1005 & RC0402FR-0724RL \\ \hline
        \end{tabular}
    \end{table}
    \newpage
    \begin{table}[H]
        \begin{tabular}{p{1.7in}|p{0.3in}|p{0.8in}|p{0.7in}|p{0.7in}|p{1in}}
        \textbf{Designator} & \textbf{QTY} & \textbf{Description} & \textbf{Comment} & \textbf{Footprint} & \textbf{Part Number} \\ \hline 
        R27, R28, R29 & 3 & RES 1M OHM 1\% 1/16W 0402 & 1 MOhms & RES 0402\_1005 & RMCF0402FT1M00 \\ \hline
        R36\_AFE\_CHANNEL\_A, R36\_AFE\_CHANNEL\_B & 2 & RES SMD 523 OHM 0.1\% 1/16W 0402 & 523 Ohms & RES 0402\_1005 & ERA-2ARB5230X \\ \hline
        R37\_AFE\_CHANNEL\_A, R37\_AFE\_CHANNEL\_B, R40\_AFE\_CHANNEL\_A, R40\_AFE\_CHANNEL\_B, R41\_AFE\_CHANNEL\_A, R41\_AFE\_CHANNEL\_B & 6 & RES SMD 500 OHM 0.05\% 1/10W 0603 & 500 Ohms & RES 0603\_1608 & TNPU0603500RAZEN00 \\ \hline
        R39\_AFE\_CHANNEL\_A, R39\_AFE\_CHANNEL\_B, R43\_AFE\_CHANNEL\_A, R43\_AFE\_CHANNEL\_B & 4 & RES 50 OHM 5\% 1/8W 0603 & 50 Ohms & RES 0603\_1608 & CH0603-50RJNTA \\ \hline
        R42\_AFE\_CHANNEL\_A, R42\_AFE\_CHANNEL\_B & 2 & RES SMD 4.02K OHM 1\% 1/10W 0603 & 4.02 kOhms & RES 0603\_1608 & AC0603FR-074K02L \\ \hline
        R44\_AFE\_CHANNEL\_A, R44\_AFE\_CHANNEL\_B & 2 & RES SMD 1K OHM 1\% 1/10W 0603 & 1 kOhms & RES 0603\_1608 & AA0603FR-071KL \\ \hline
        R45\_AFE\_CHANNEL\_A, R45\_AFE\_CHANNEL\_B & 2 & RES 25 OHM 0.1\% 1/20W 0402 & 25 Ohms & RES 0402\_1005 & FC0402E25R0BST0 \\ \hline
        S1 & 1 & SWITCH PUSH SPST-NO 0.4VA 28V & &  & AB11AH-HA \\ \hline
        TP1, TP2, TP3, TP4, TP5, TP9, TP24, TP25, TP26, TP45, TP46, TP47, TP48, TP50, TP51, TP52, TP53, TP54, TP55, TP56 & 20 & Test Point, 1 Position SMD, RoHS, Tape and Reel & 5019 & KSTN5019 & 5019 \\ \hline
        U1 & 1 & IC HS USB TO UART/FIFO 48QFN & FT232 & QFN-48 & FT232HQ-REEL \\ \hline
        \end{tabular}
    \end{table}
    \newpage
    \begin{table}[H]
        \begin{tabular}{p{1.7in}|p{0.3in}|p{0.8in}|p{0.7in}|p{0.7in}|p{1in}}
        \textbf{Designator} & \textbf{QTY} & \textbf{Description} & \textbf{Comment} & \textbf{Footprint} & \textbf{Part Number} \\ \hline 
        U2 & 1 & Dual 8-Bit AD Converter with Parallel Interface, 40MSPS, -40 to +85 degC, ST-48, Pb-Free, Tray &  & ST-48M & AD9288BSTZ-40 \\ \hline
        U3\_AFE\_CHANNEL\_A, U3\_AFE\_CHANNEL\_B & 2 & IC ADC DRIVER 8SOIC & AD8138 & R-8-IPC\_A & AD8138ARZ-R7 \\ \hline
        U5 & 1 & Fixed Low Drop Positive Voltage Regulator, 3.3V, 3-Pin TO-220 & LD1117 & TO220 & LD1117V33C \\ \hline
        U6 & 1 & 2K, 128x16-bit, 2.5V Microwire Serial EEPROM, 8-Pin SOIC 150mil, Commercial Temperature, Tape and Reel & 93LC56 & SOIC8 & 93LC56BT/SN \\ \hline
        U7 & 1 & CURRENT SENSOR & ACS720 &  & ACS720KLATR-15AB-T \\ \hline
        Y1 & 1 & CRYSTAL 12.0000MHZ 20PF SMD & 12 MHz & ABLS & ABLS-12.000MHZ-20-B-3-H-T \\ \hline
        \end{tabular}
    \end{table}

    % TODO: needs smaller font size or line wrapping
    \section{TeachEE SystemVerilog RTL Code} \label{appendix:rtl-code}
    This appendix contains all the SystemVerilog RTL files in the TeachEE
    project. Each subsection corresponds to the files in a particular folder of
    the GitHub repository.

    \subsubsection{TeachEE Main Project Top Level Module}
    \inputminted[linenos,breaklines]{systemverilog}{../../rtl/teachee/teachee.sv}

    \subsection{AXIS} \label{appendix:axis}
    \subsubsection{axis\_adapter\_wrapper.sv}
    \inputminted[linenos,breaklines]{systemverilog}{../../rtl/axis/axis_adapter_wrapper.sv}
    \subsubsection{axis\_async\_fifo\_wrapper.sv}
    \inputminted[linenos,breaklines]{systemverilog}{../../rtl/axis/axis_async_fifo_wrapper.sv}
    \subsubsection{axis\_interface.sv} \label{appendix:axis-interface}
    \inputminted[linenos,breaklines]{systemverilog}{../../rtl/axis/axis_interface.sv}

    \subsection{COBS}
    \subsubsection{cobs\_axis\_adapter\_wrapper.sv}
    \inputminted[linenos,breaklines]{systemverilog}{../../rtl/cobs/cobs_axis_adapter_wrapper.sv}
    \subsubsection{cobs\_encode\_wrapper.sv}
    \inputminted[linenos,breaklines]{systemverilog}{../../rtl/cobs/cobs_encode_wrapper.sv}

    \subsection{FT232H}
    \subsubsection{ft232h.sv}
    \inputminted[linenos,breaklines]{systemverilog}{../../rtl/ft232h/ft232h.sv}
    \subsubsection{ft232h\_bfm.sv}
    \inputminted[linenos,breaklines]{systemverilog}{../../rtl/ft232h/ft232h_bfm.sv}
    \subsubsection{ft232h\_package.sv}
    \inputminted[linenos,breaklines]{systemverilog}{../../rtl/ft232h/ft232h_package.sv}

    \subsection{HSADC}
    \subsubsection{hsadc\_axis\_wrapper.sv}
    \inputminted[linenos,breaklines]{systemverilog}{../../rtl/hsadc/hsadc_axis_wrapper.sv}
    \subsubsection{hsadc\_bfm.sv}
    \inputminted[linenos,breaklines]{systemverilog}{../../rtl/hsadc/hsadc_bfm.sv}
    \subsubsection{hsadc\_interface.sv}
    \inputminted[linenos,breaklines]{systemverilog}{../../rtl/hsadc/hsadc_interface.sv}

    \subsection{Xilinx XADC} \label{xadc-bfm}
    \subsubsection{xadc\_bfm.sv}
    \inputminted[linenos,breaklines]{systemverilog}{../../rtl/xadc/xadc_bfm.sv}
    \subsubsection{xadc\_drp\_axis\_adapter.sv}
    \inputminted[linenos,breaklines]{systemverilog}{../../rtl/xadc/xadc_drp_axis_adapter.sv}
    \subsubsection{xadc\_drp\_axis\_single\_stream.sv}
    \inputminted[linenos,breaklines]{systemverilog}{../../rtl/xadc/xadc_drp_axis_single_stream.sv}
    \subsubsection{xadc\_drp\_package.sv}
    \inputminted[linenos,breaklines]{systemverilog}{../../rtl/xadc/xadc_drp_package.sv}
    \subsubsection{xadc\_packetizer.sv}
    \inputminted[linenos,breaklines]{systemverilog}{../../rtl/xadc/xadc_packetizer.sv}

    \subsection{Legacy Non-VUnit Testbenches} \label{appendix:rtl-leg-tb}
    \subsubsection{ft232h\_bfm\_tb.sv}
    \inputminted[linenos,breaklines]{systemverilog}{../../rtl/testbenches/legacy/ft232h_bfm_tb.sv}
    \subsubsection{ft232h\_tb.sv}
    \inputminted[linenos,breaklines]{systemverilog}{../../rtl/testbenches/legacy/ft232h_tb.sv}
    \subsubsection{xadc\_bfm\_tb.sv}
    \inputminted[linenos,breaklines]{systemverilog}{../../rtl/testbenches/legacy/xadc_bfm_tb.sv}
    \subsubsection{xadc\_drp\_axis\_adapter\_tb.sv}
    \inputminted[linenos,breaklines]{systemverilog}{../../rtl/testbenches/legacy/xadc_drp_axis_adapter_tb.sv}
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

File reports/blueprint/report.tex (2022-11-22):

\documentclass[letterpaper,12pt]{article}
\usepackage[parfill]{parskip} % Remove paragraph indentation
\usepackage{amsmath}
\usepackage{float}
\usepackage[margin=1in]{geometry}
\usepackage{graphicx}
\usepackage{placeins}
\usepackage{siunitx}
\usepackage[title]{appendix}
\usepackage{pdflscape}
\usepackage{tabularx}
\usepackage{times}
\usepackage{url}
\usepackage{setspace}
\usepackage[none]{hyphenat}
\usepackage{pdfpages}
\usepackage{longtable}
\usepackage{tikz}

\DeclareSIUnit{\samplepersec}{SPS}

\begin{document}

\begin{titlepage}
    \begin{center}
        \vspace*{1cm}

        \Large
        \textbf{ELEC 490/498 Project Blueprint Document}

        \vspace{0.5cm}
        Group 18\\
        TeachEE\\
        \vspace{0.5cm}
        \normalsize
        \textbf{John Giorshev (20103586, john.giorshev@queensu.ca) \\ Eric Yang (20120750, e.yang@queensu.ca) \\ Ethan Peterson (20105011, 17emp5@queensu.ca) \\ Timothy Morland (20096286, 17tm22@queensu.ca)}\\
        \vspace{0.5cm}
        Submitted November 22, 2022\\

        \vfill
            
        \textbf{To:}\\
        Instructor Dr. Michael Korenberg (korenber@queensu.ca) \\
        Instructor Dr. Alireza Bakhshai (alireza.bakhshai@queensu.ca) \\
        Instructor Dr. Alex Tait (alex.tait@queensu.ca) \\
        Instructor and Supervisor Dr. Sean Whitehall (sw109@queensu.ca) \\
        Supervisor Dr. Thomas Dean (tom.dean@queensu.ca) \\
            
        \vspace{1.8cm}

    \end{center}
\end{titlepage}
\setstretch{1.5}
\pagenumbering{gobble}
\section*{Executive Summary}
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

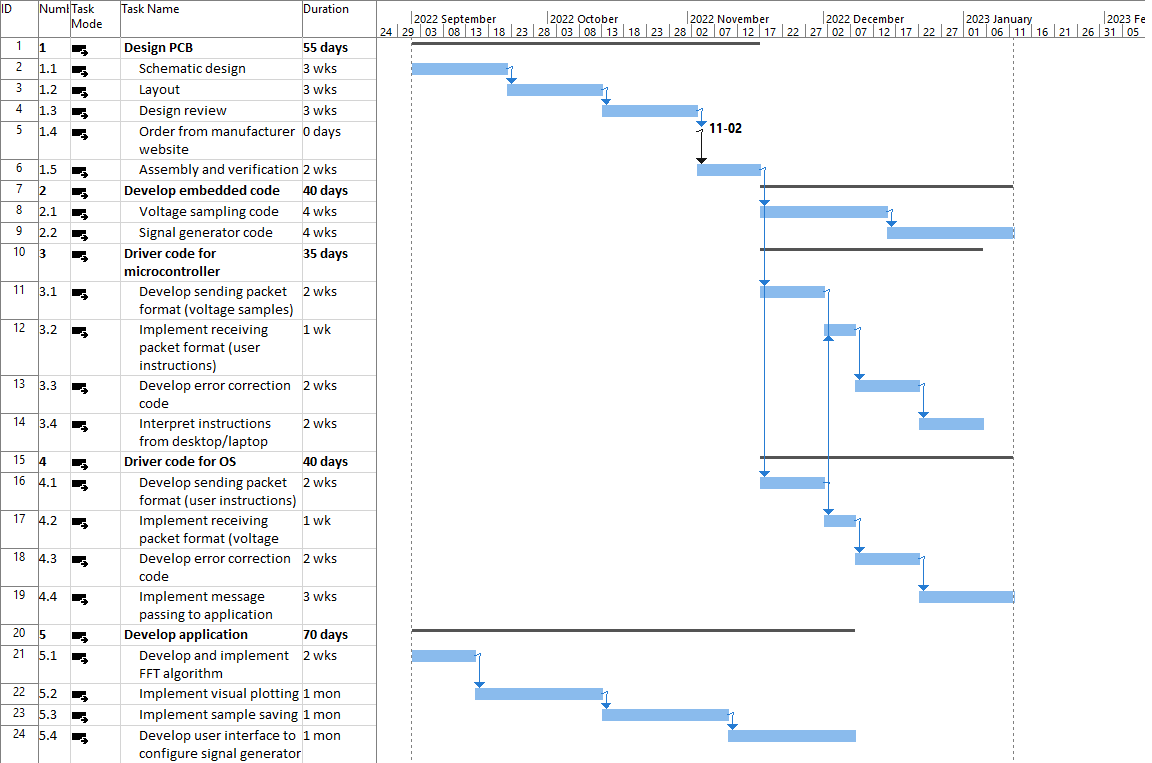
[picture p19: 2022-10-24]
reports/proposal/report/figures/gantt.png

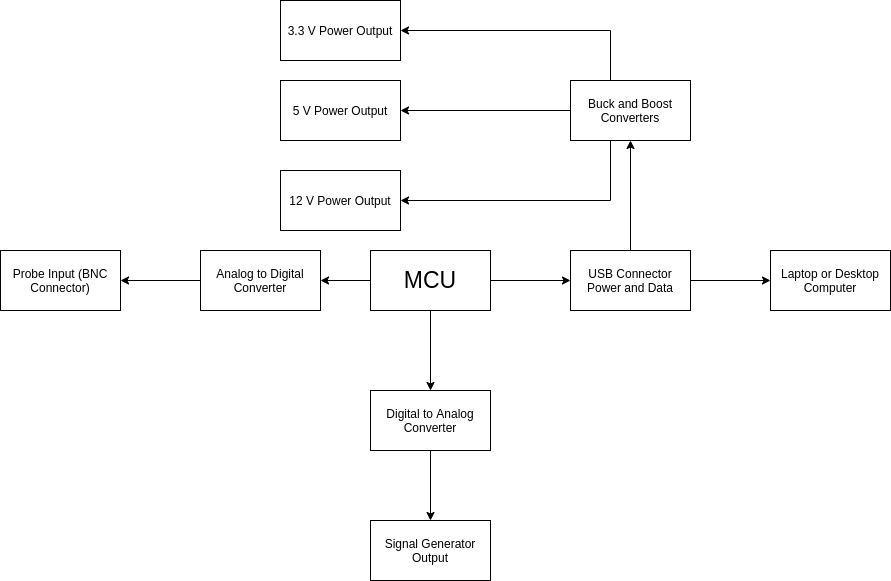
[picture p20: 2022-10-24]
reports/proposal/report/figures/pcb-block-diagram.png

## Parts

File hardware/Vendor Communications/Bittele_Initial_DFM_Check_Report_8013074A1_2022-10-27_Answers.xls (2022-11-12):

 |  |  | Initial Design for Manufacturing Check Report |  |  |  |  |  |  |  | Form No:
 |  |  |  |  |  |  |  |  |  |  | BTL- DFM-001
Product # |  | Customer ID |  | Purchase Order | Quantity | Checked by |  |  | Audit by
 |  |  |  |  |  | Name | Date | Time (Hour) | Name | Date
8013074A1 |  |  |  | None |  |  | 2022-10-27
Gerber File |  |  |  | X-Y Coordinate File |  | Drill File |  | BOM check |  | Others
Note: If you have BOM change requests, please send the list of change details instead of sending an updated(new) BOM for quick turnaround. We will ignore the BOM in any zip file unless being requested.
Quiz# | Question Description |  |  |  |  | Illustration |  |  |  |  | Client Reply
1 | In gerber, ref designators of some parts are not given in silk screen. Please either update gerber by adding all ref designators or provide us assembly drawing having all ref designators. The image at right is an example of assembly drawing. |  |  |  |  |  |  |  |  |  | I have attached an assembly drawing to this message
2 | #14_D1,D3 p/n:APTL3216QBC/D-01, #15_D2,D5 p/n:APTL3216ZGCK-01 As per datasheet, these LEDs are placed Upside down in reel and it seems you want the Lens of led to be facing upward, therefore these leds can not be pick and placed by machine and we have to manually mount it. If possible, please change the p/n. |  |  |  |  |  |  |  |  |  | Please replace with 5990291007F (https://www.digikey.ca/en/products/detail/dialight/5990291007F/9385421)
3 | We find a non-closed polygon indicated by an arrow in gm1 layer.Please confirm whether it needs to be made into non-plated slot? Suggestion A: Ignore it and delete this non-closed polygon. Suggestion B: Need made it into non-plated slot and shave coppers 0.25mm away from the slot on g1 and g2 layer as picture-2 shown. |  |  |  |  |  |  |  |  |  | Please follow suggestion A
4 | The designed copper extends to the edge of the board. It will cause copper exposure and burr if we follow Gerber. Suggestion A: Shave coppers 0.25mm away from the outline to avoid copper exposure. Suggestion B: Follow Gerber to build, exposed copper and burr are both acceptable. |  |  |  |  |  |  |  |  |  | Please go with Suggestion A

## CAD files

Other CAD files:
hardware/cad/teachee_tray.f3d
hardware/cad/teachee_tray.f3z

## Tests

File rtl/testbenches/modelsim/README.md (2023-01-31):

# Modelsim `.do` Files
When loading up modelsim from VUnit, no signals are loaded into the waveform viewer by default. This folder contains the configs I use to debug certain testbenches. Currently, you need to do File > Load Format, but I am looking at a way to automate this as well.

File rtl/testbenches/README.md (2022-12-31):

# TeachEE Testbenches

This directory contains RTL code for the VUNIT testbenches and the `legacy`
folder holds the testbenches written before the implementation of VUNIT.

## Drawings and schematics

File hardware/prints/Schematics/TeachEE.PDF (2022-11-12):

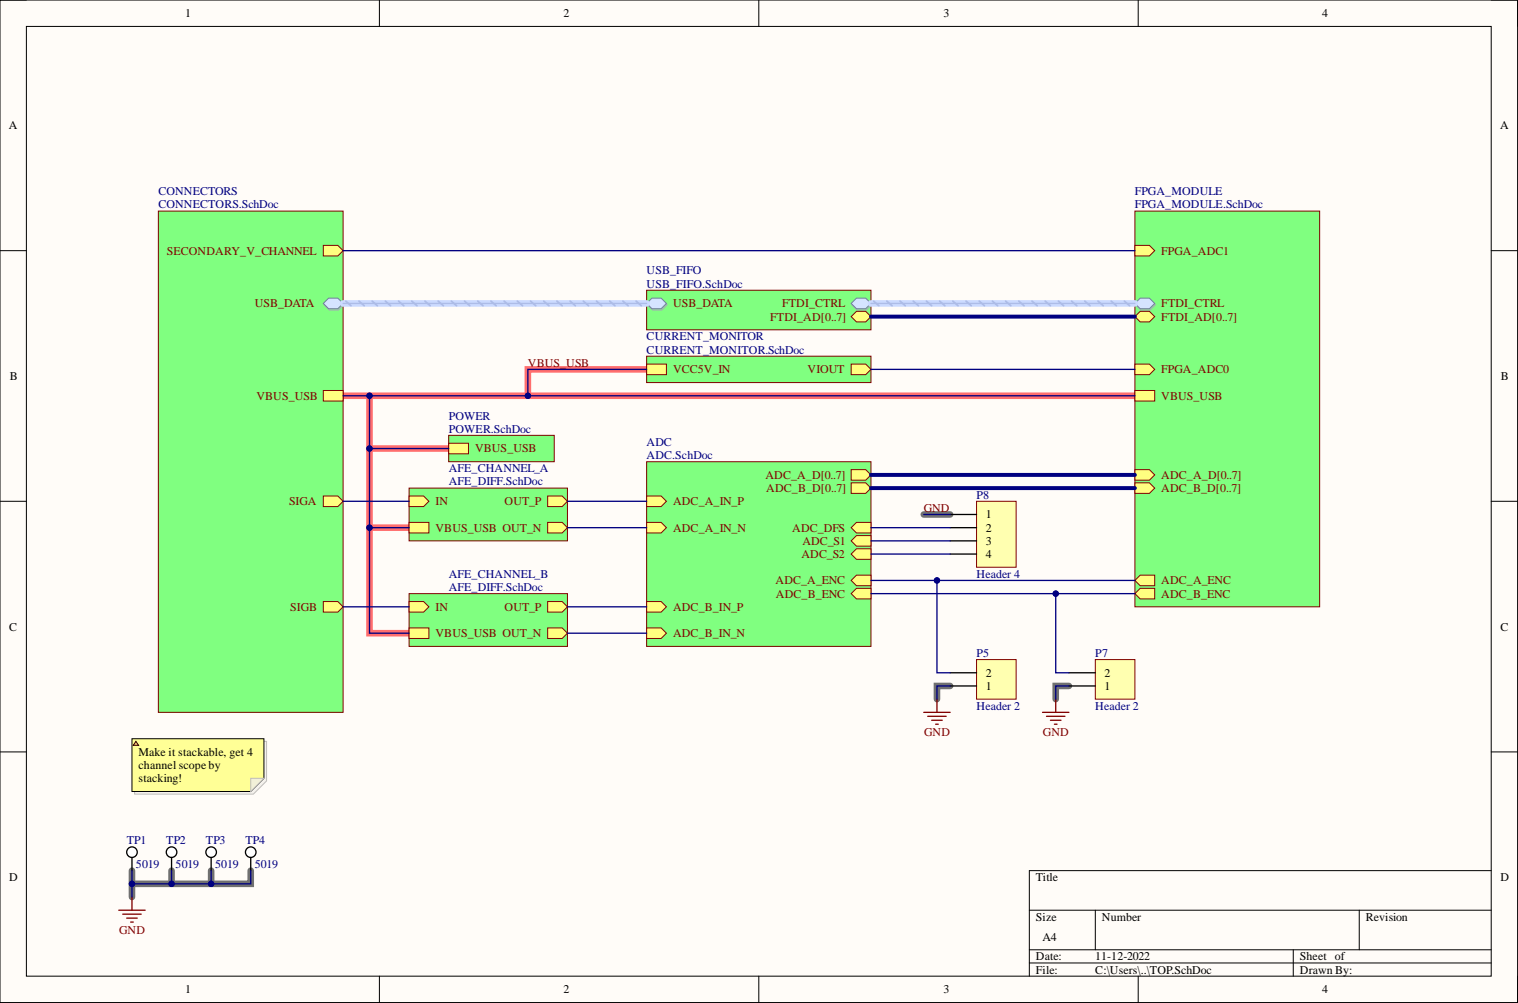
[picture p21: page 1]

Make it stackable, get 4
channelscope by
stacking!

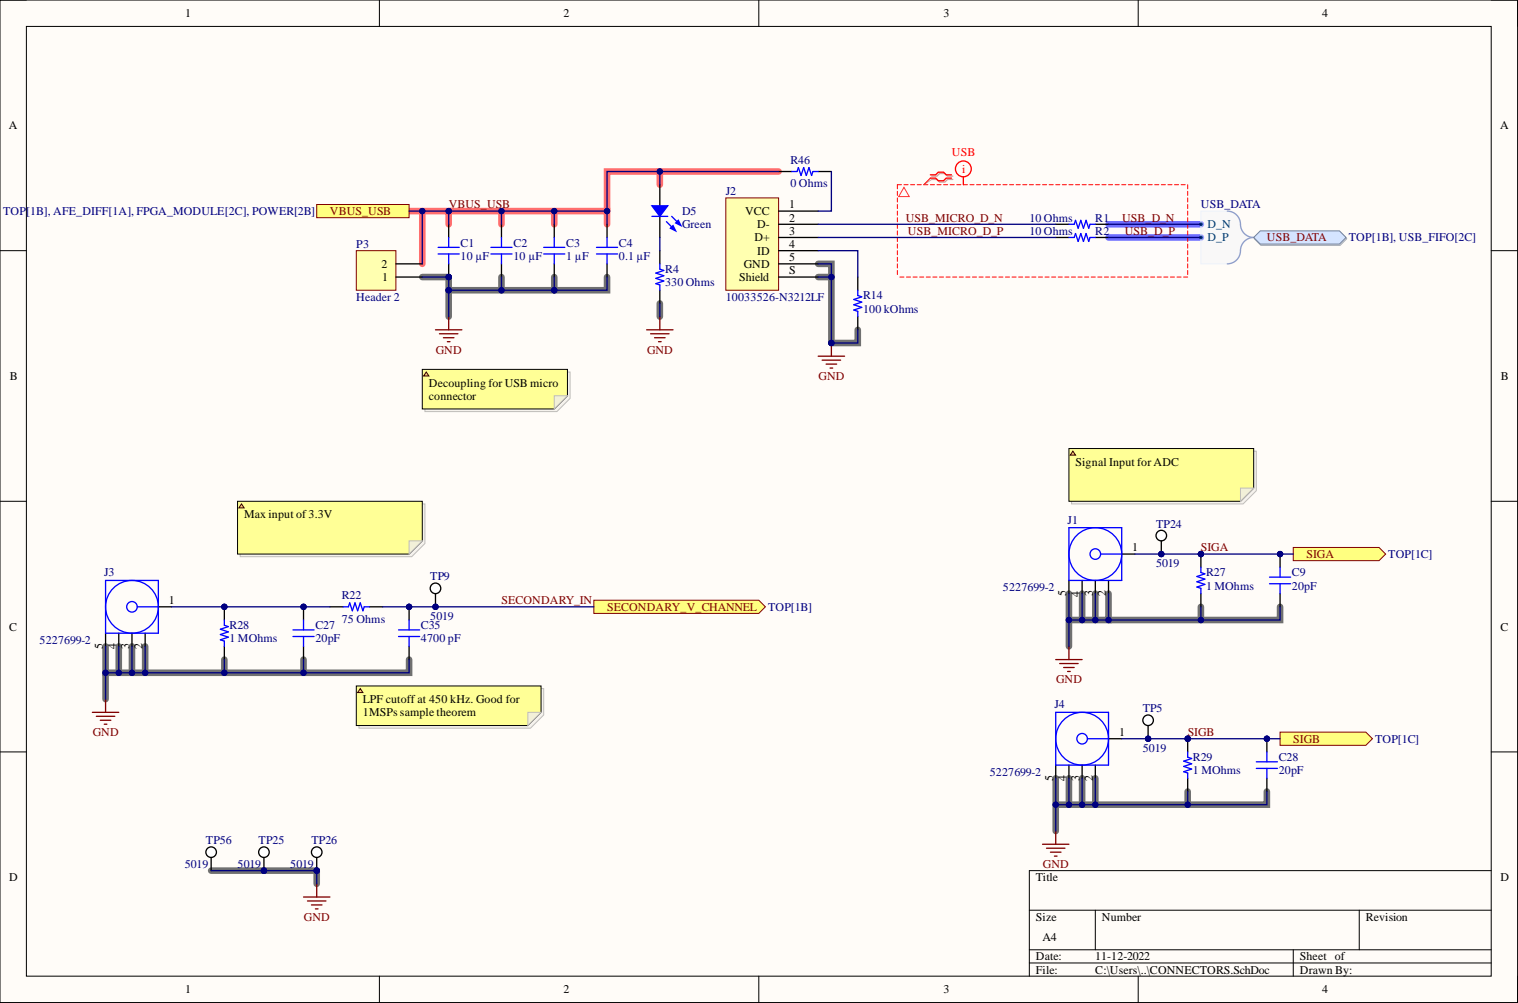
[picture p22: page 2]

Decoupling for USB micro
connector

Signal Input for ADC

LPF cutoff at 450 kHz. Good for
1MSPssample theorem

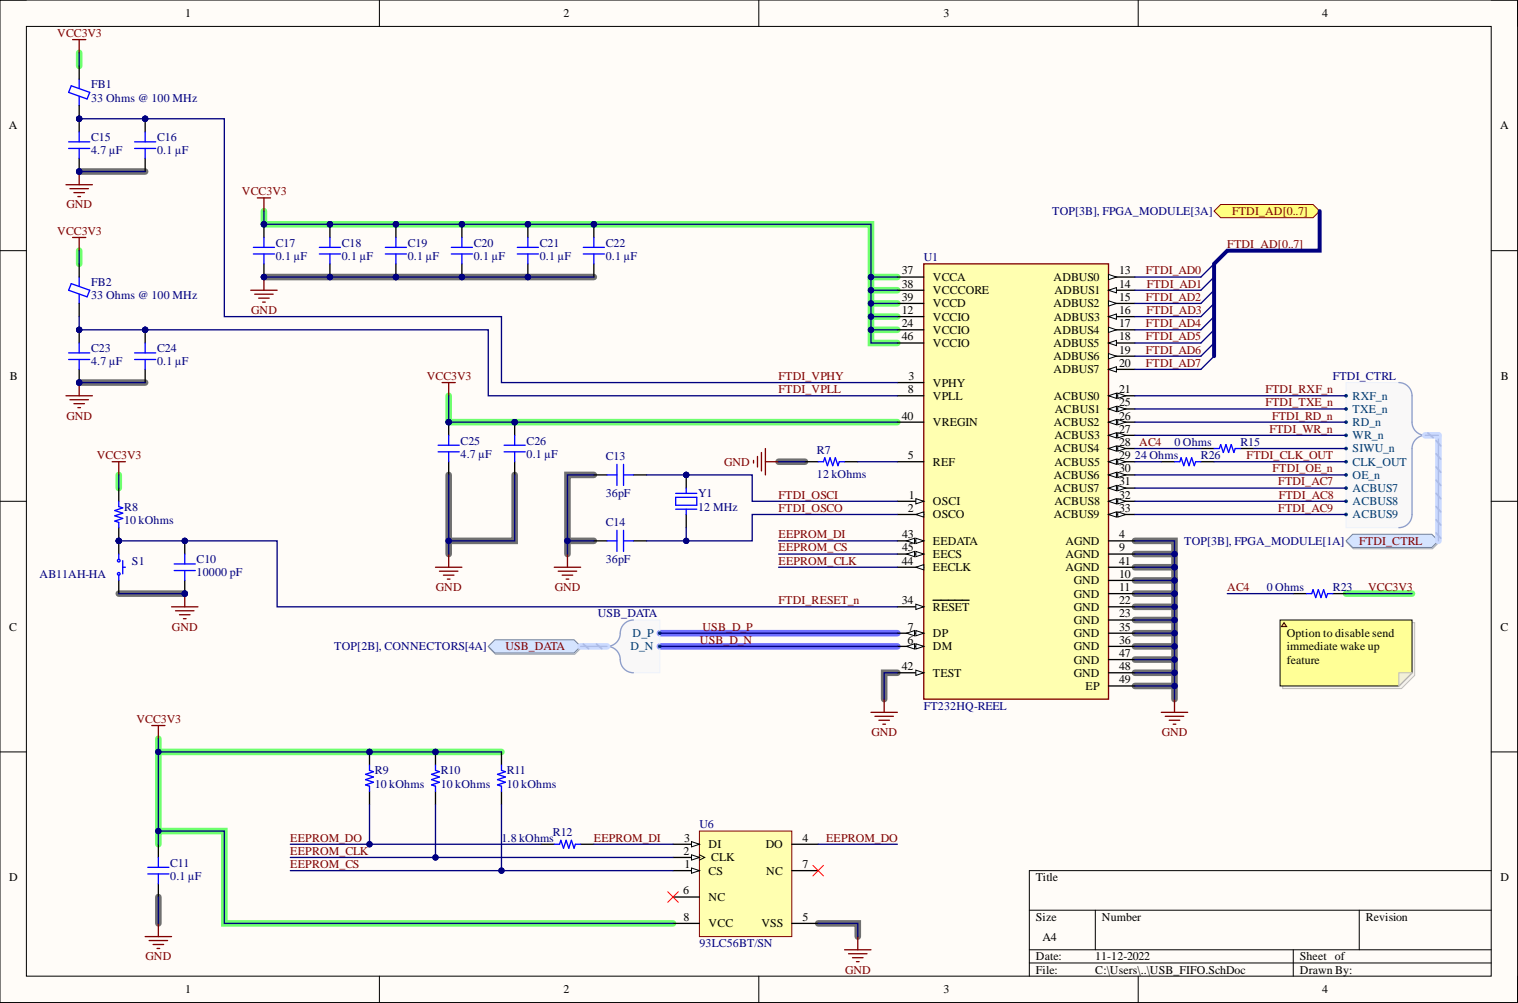
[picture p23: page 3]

EEPROM_DI

EECLK 44 EECS 45 EEDATA 43 RESET 34

Option to disable send
immediate wake up
feature

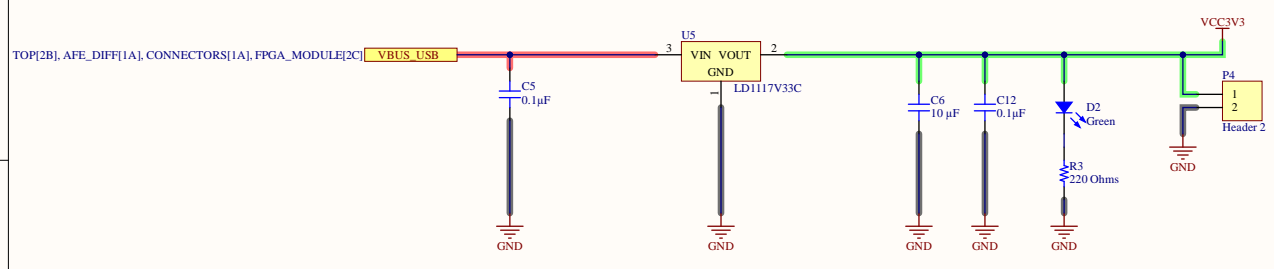
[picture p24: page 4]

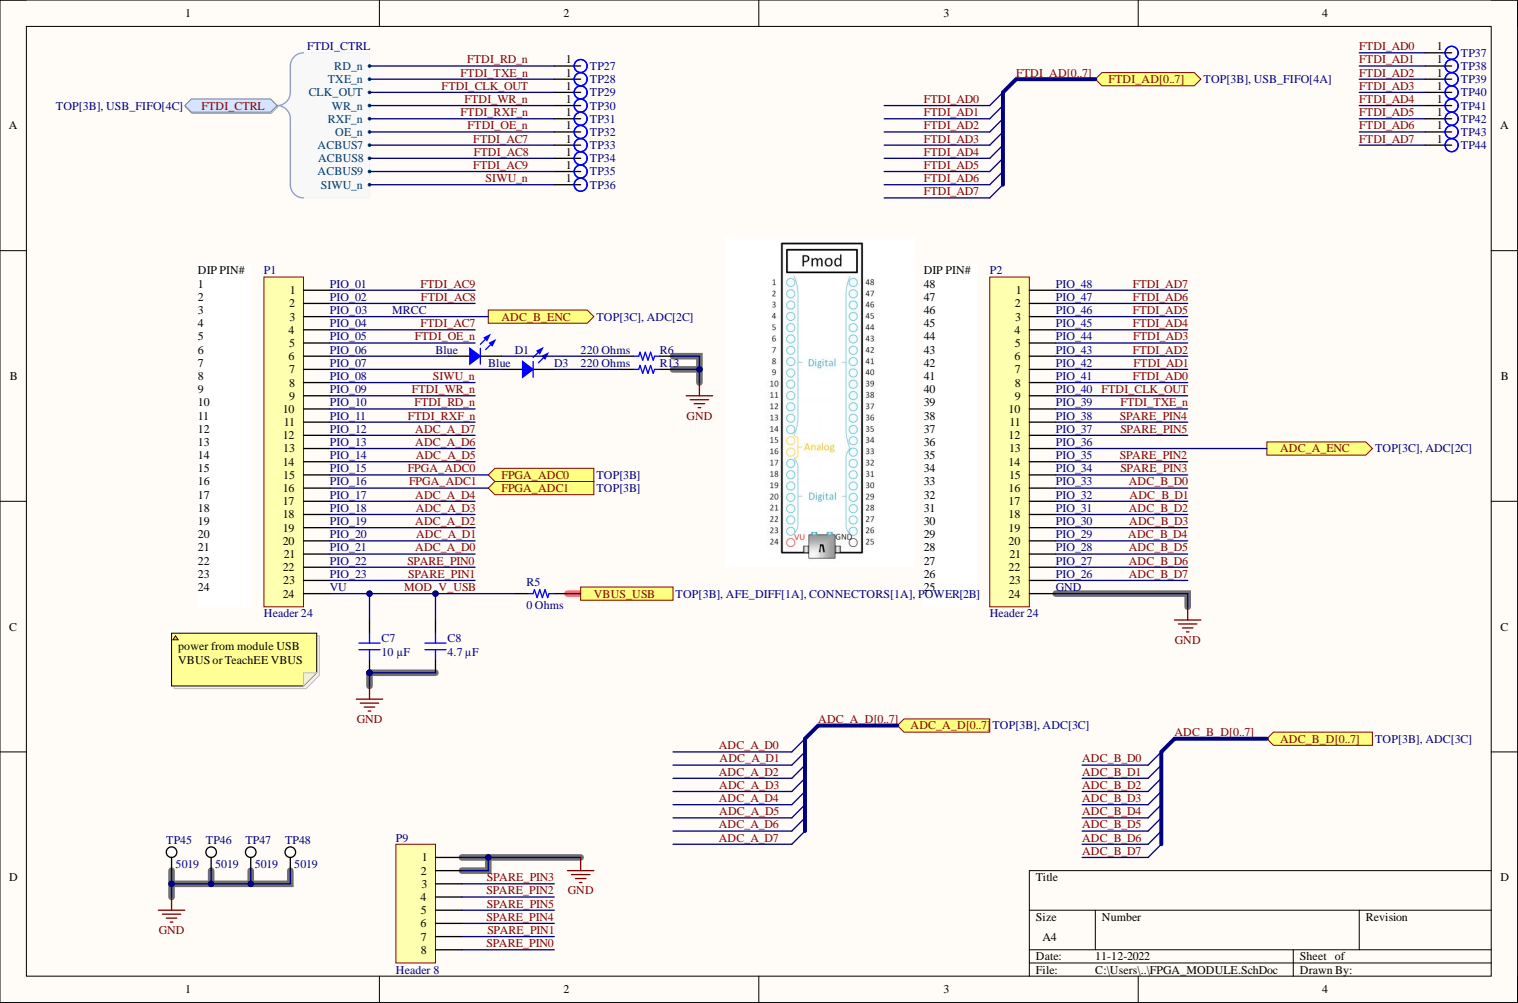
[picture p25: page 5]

power from module USB
VBUS or TeachEE VBUS

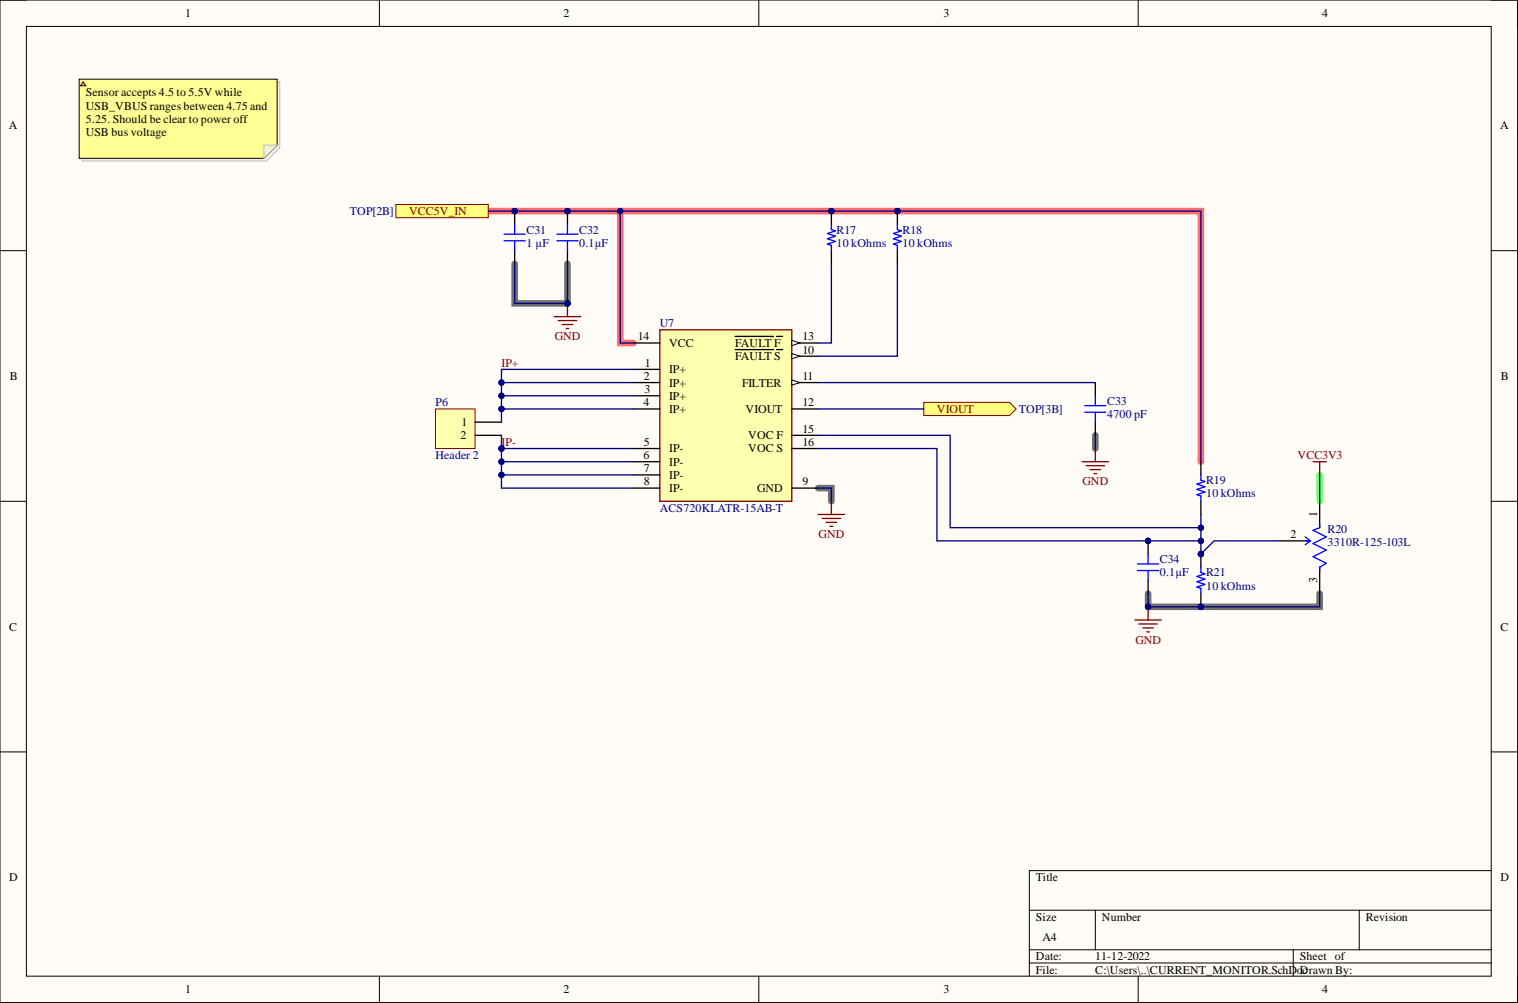
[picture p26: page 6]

7 | | G N D

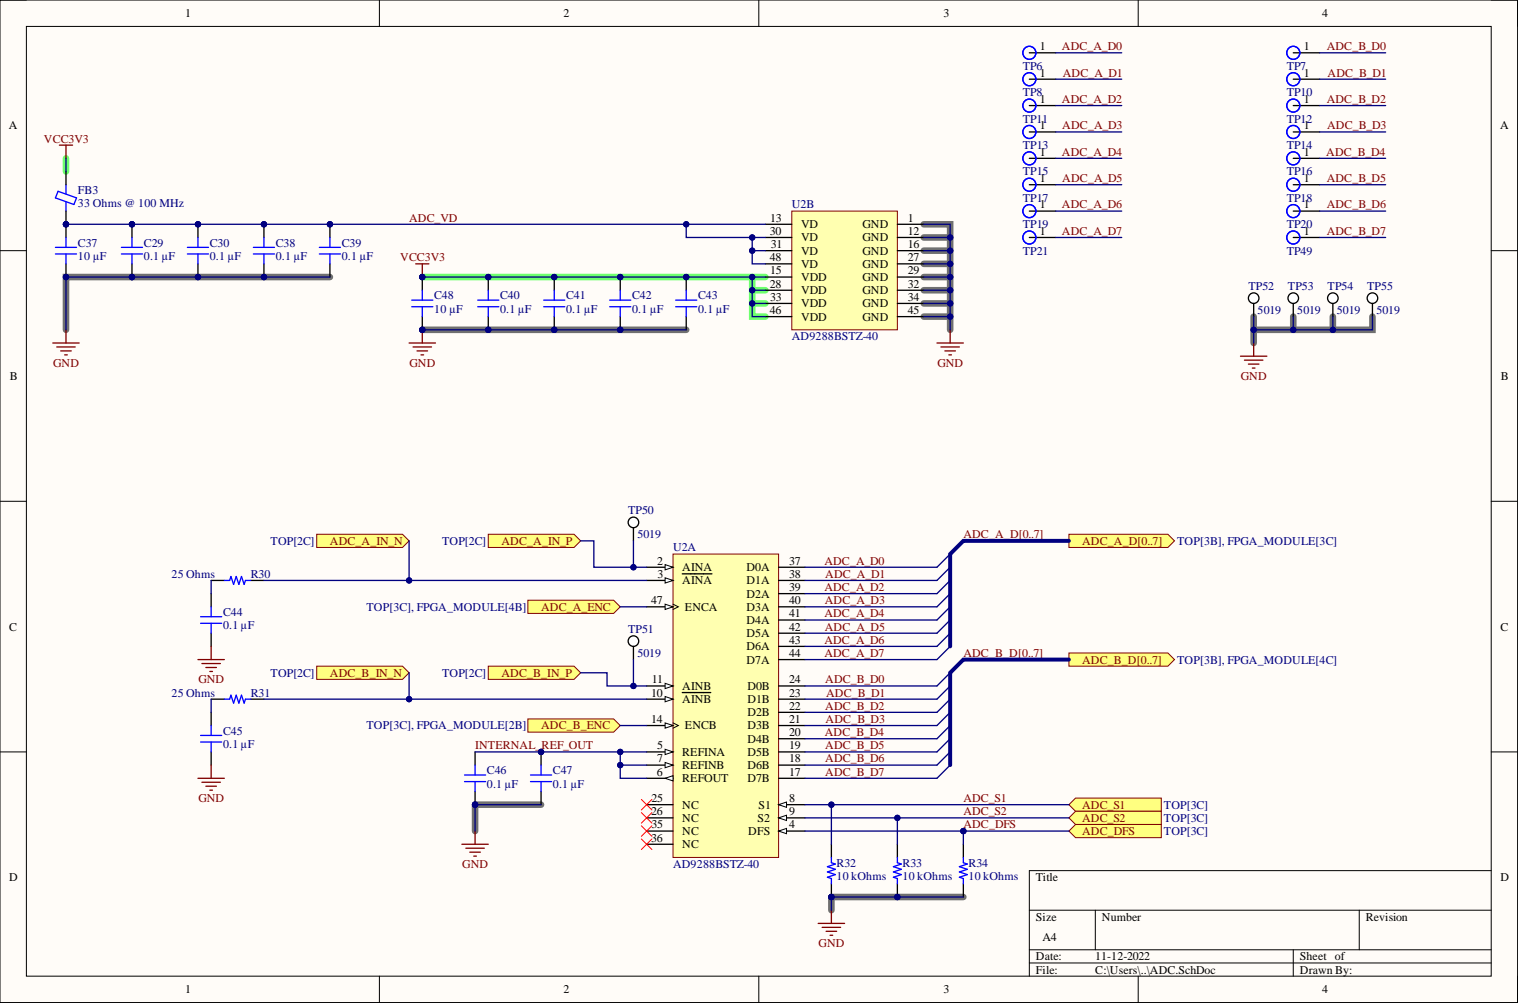
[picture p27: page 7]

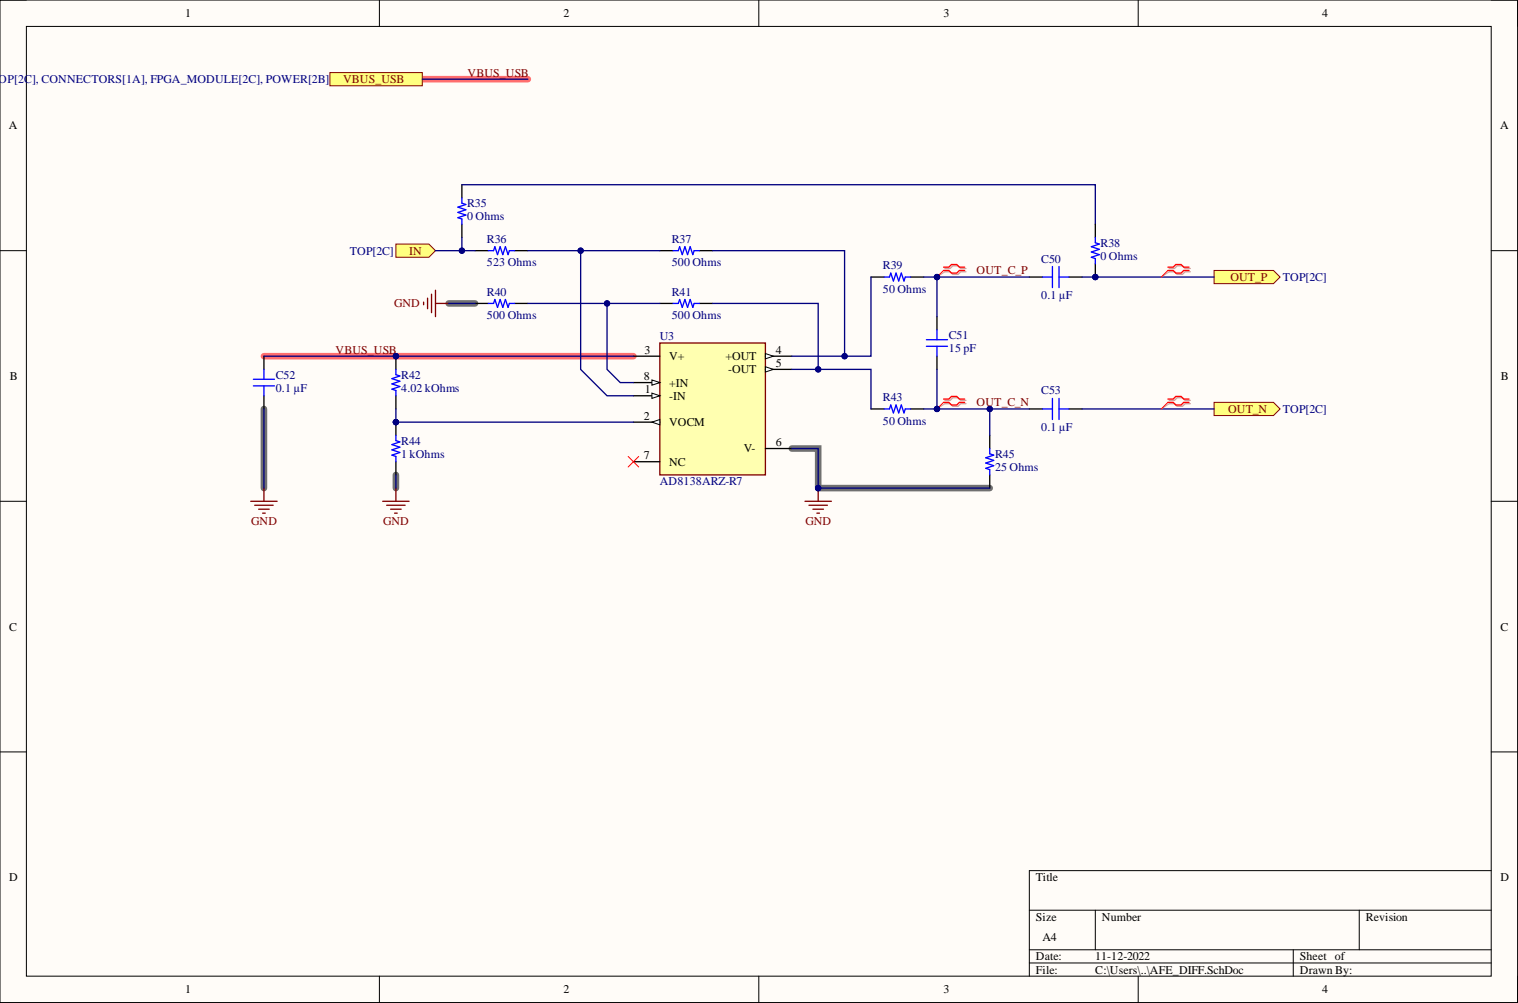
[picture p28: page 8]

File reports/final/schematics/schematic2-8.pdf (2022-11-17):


Decoupling for USB micro
connector

Signal Input for ADC

LPF cutoff at 450 kHz. Good for
1MSPssample theorem


Option to disable send
immediate wake up
feature

Size; umb; Rev; Dat; Sheet; sers; ER.Sch; Draw; 2 Green; AFE; DIFF[1; ECT; ORS[1; A], FPG; VBUS_; hms; P4Header; VCC3

1 | TP27 1 | TP28 1 | TP29 1 | TP30 1 | TP31 1 | TP32 1 | TP33 1 | TP34 1 | TP35 1 | TP36
1 | TP37 1 | TP38 1 | TP39 1 | TP40 1 | TP41 1 | TP42 1 | TP43 1 | TP44


power from module USB
VBUS or TeachEE VBUS

Size; umb; Rev; \..\CURRE; NIT; oDcraw; VCC; FILT; VIO; ACS7; ATR-1; VCC5; hms; P6Header; VCC3; Sen; or accep; USB_; VBUS ran; ges; bet; ween; be clear; wer; off; USB; tag


Size; umb; Rev; AFE; DIFF.Sc; Draw; hms; ECT; ORS[1; A], FPG; VBUS_

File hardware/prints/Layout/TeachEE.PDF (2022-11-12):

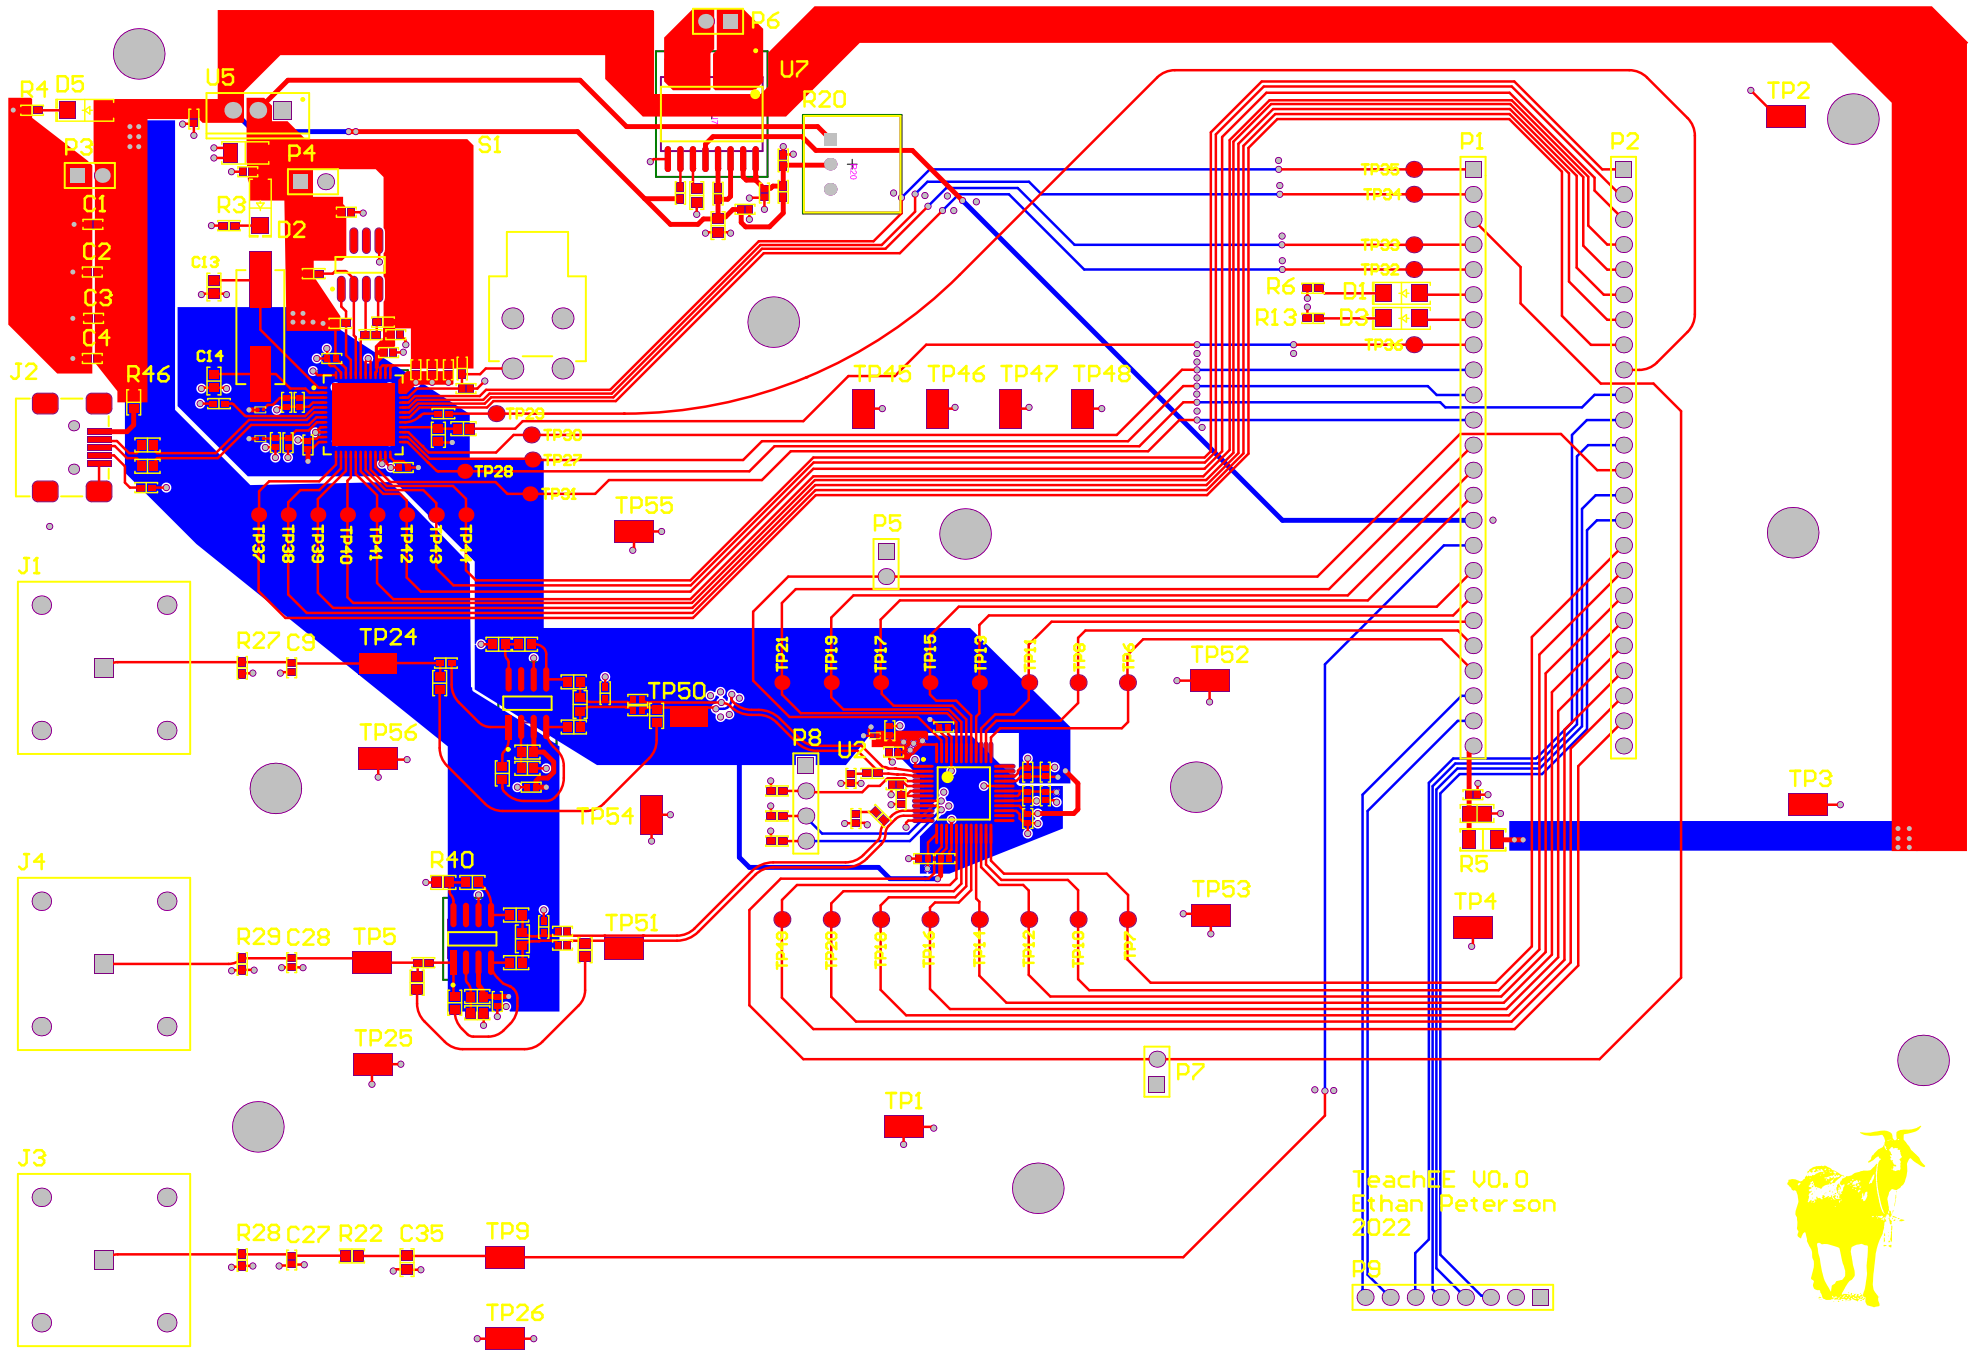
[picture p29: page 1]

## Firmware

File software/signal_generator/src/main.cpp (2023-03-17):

#include <EasyButton.h>

#include "signals.h"

#define X_PIN A0
#define Y_PIN A1
#define BUTTON_PIN A2

uint32_t t = 0;
uint8_t f = 0;

EasyButton button(BUTTON_PIN, true, true, false);

void handle_button() {
    f += 1;

    if (f >= NUM_FUNCS) {
      f = 0;
    }
}

void setup() {
  button.begin();
  button.onPressed(handle_button);

  analogWriteResolution(12);
}

void loop() {
  button.read();

  t += 1;
  if (t >= NUM_TIMES) {
    t = 0;
  }

  uint32_t a = analogRead(A0) >> 4;

  uint32_t out = signals[f][a][t];
  analogWrite(DAC0, out);

  uint32_t delay = analogRead(A1) >> 4;
  delayMicroseconds(delay);
}

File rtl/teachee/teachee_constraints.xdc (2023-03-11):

## This file is a general .xdc for the CmodA7 rev. B
## To use it in a project:
## - uncomment the lines corresponding to used pins
## - rename the used ports (in each line, after get_ports) according to the top level signal names in the project

## 12 MHz Clock Signal
set_property -dict { PACKAGE_PIN L17   IOSTANDARD LVCMOS33 } [get_ports { cmod_osc }]; #IO_L12P_T1_MRCC_14 Sch=gclk
create_clock -add -name cmod_osc -period 83.33 -waveform {0 41.66} [get_ports {cmod_osc}];

## FTDI232Hq Clock Output
set_property -dict { PACKAGE_PIN W4    IOSTANDARD LVCMOS33 } [get_ports { ftdi_clk }]; #IO_L12N_T1_MRCC_34 Sch=pio[40]
create_clock -add -name ftdi_clk -period 16.67 -waveform {0 8.33} [get_ports {ftdi_clk}];
set_property CLOCK_DEDICATED_ROUTE FALSE [get_nets {ftdi_clk_IBUF}]

# set_property -dict { PACKAGE_PIN W5    IOSTANDARD LVCMOS33 } [get_ports { ftdi_clk }]; #IO_L12P_T1_MRCC_34 Sch=pio[36]

# Create clocks for the PLL outputs
# create_clock -add -name clk_100_pin -period 10.0 -waveform {0 5.0} [get_nets {clk_100}];
# create_clock -add -name clk_50_pin -period 20.0 -waveform {0 10.0} [get_nets {clk_50}];
# create_clock -add -name clk_25_pin -period 40.0 -waveform {0 20.0} [get_nets {clk_25}];
# create_clock -add -name clk_20_pin -period 50.0 -waveform {0 25.0} [get_nets {clk_20}];
# create_generated_clock -name clk_10_pin [get_nets {clk_10}];


# Mark all clocks as async to one another
set_clock_groups -group cmod_osc -group ftdi_clk -group clk_10_teachee_pll -group clkfbout_teachee_pll -group clk_100_teachee_pll -asynchronous


## LEDs
set_property -dict { PACKAGE_PIN A17   IOSTANDARD LVCMOS33 } [get_ports { led[0] }]; #IO_L12N_T1_MRCC_16 Sch=led[1]
set_property -dict { PACKAGE_PIN C16   IOSTANDARD LVCMOS33 } [get_ports { led[1] }]; #IO_L13P_T2_MRCC_16 Sch=led[2]

## RGB LED
#set_property -dict { PACKAGE_PIN B17   IOSTANDARD LVCMOS33 } [get_ports { led0_b }]; #IO_L14N_T2_SRCC_16 Sch=led0_b
#set_property -dict { PACKAGE_PIN B16   IOSTANDARD LVCMOS33 } [get_ports { led0_g }]; #IO_L13N_T2_MRCC_16 Sch=led0_g
#set_property -dict { PACKAGE_PIN C17   IOSTANDARD LVCMOS33 } [get_ports { led0_r }]; #IO_L14P_T2_SRCC_16 Sch=led0_r

## Buttons
set_property -dict { PACKAGE_PIN A18   IOSTANDARD LVCMOS33 } [get_ports { btn[0] }]; #IO_L19N_T3_VREF_16 Sch=btn[0]
set_property -dict { PACKAGE_PIN B18   IOSTANDARD LVCMOS33 } [get_ports { btn[1] }]; #IO_L19P_T3_16 Sch=btn[1]

## Pmod Header JA
#set_property -dict { PACKAGE_PIN G17   IOSTANDARD LVCMOS33 } [get_ports { ja[0] }]; #IO_L5N_T0_D07_14 Sch=ja[1]
#set_property -dict { PACKAGE_PIN G19   IOSTANDARD LVCMOS33 } [get_ports { ja[1] }]; #IO_L4N_T0_D05_14 Sch=ja[2]
#set_property -dict { PACKAGE_PIN N18   IOSTANDARD LVCMOS33 } [get_ports { ja[2] }]; #IO_L9P_T1_DQS_14 Sch=ja[3]
#set_property -dict { PACKAGE_PIN L18   IOSTANDARD LVCMOS33 } [get_ports { ja[3] }]; #IO_L8P_T1_D11_14 Sch=ja[4]
#set_property -dict { PACKAGE_PIN H17   IOSTANDARD LVCMOS33 } [get_ports { ja[4] }]; #IO_L5P_T0_D06_14 Sch=ja[7]
#set_property -dict { PACKAGE_PIN H19   IOSTANDARD LVCMOS33 } [get_ports { ja[5] }]; #IO_L4P_T0_D04_14 Sch=ja[8]
#set_property -dict { PACKAGE_PIN J19   IOSTANDARD LVCMOS33 } [get_ports { ja[6] }]; #IO_L6N_T0_D08_VREF_14 Sch=ja[9]
#set_property -dict { PACKAGE_PIN K18   IOSTANDARD LVCMOS33 } [get_ports { ja[7] }]; #IO_L8N_T1_D12_14 Sch=ja[10]

## Analog XADC Pins
## Only declare these if you want to use pins 15 and 16 as single ended analog inputs. pin 15 -> vaux4, pin16 -> vaux12
set_property -dict { PACKAGE_PIN G2    IOSTANDARD LVCMOS33 } [get_ports { xa_n[0] }]; #IO_L1N_T0_AD4N_35 Sch=ain_n[15]
set_property -dict { PACKAGE_PIN G3    IOSTANDARD LVCMOS33 } [get_ports { xa_p[0] }]; #IO_L1P_T0_AD4P_35 Sch=ain_p[15]
set_property -dict { PACKAGE_PIN J2    IOSTANDARD LVCMOS33 } [get_ports { xa_n[1] }]; #IO_L2N_T0_AD12N_35 Sch=ain_n[16]
set_property -dict { PACKAGE_PIN H2    IOSTANDARD LVCMOS33 } [get_ports { xa_p[1] }]; #IO_L2P_T0_AD12P_35 Sch=ain_p[16]

## GPIO Pins
## Pins 15 and 16 should remain commented if using them as analog inputs
#set_property -dict { PACKAGE_PIN M3    IOSTANDARD LVCMOS33 } [get_ports { pio1  }]; #IO_L8N_T1_AD14N_35 Sch=pio[01]
#set_property -dict { PACKAGE_PIN L3    IOSTANDARD LVCMOS33 } [get_ports { pio2  }]; #IO_L8P_T1_AD14P_35 Sch=pio[02]
set_property -dict { PACKAGE_PIN A16   IOSTANDARD LVCMOS33 } [get_ports { hsadc_b_enc  }]; #IO_L12P_T1_MRCC_16 Sch=pio[03]
#set_property -dict { PACKAGE_PIN K3    IOSTANDARD LVCMOS33 } [get_ports { pio4  }]; #IO_L7N_T1_AD6N_35 Sch=pio[04]
set_property -dict { PACKAGE_PIN C15   IOSTANDARD LVCMOS33 } [get_ports { ftdi_oe_n  }]; #IO_L11P_T1_SRCC_16 Sch=pio[05]
set_property -dict { PACKAGE_PIN H1    IOSTANDARD LVCMOS33 } [get_ports { teachee_led[0]  }]; #IO_L3P_T0_DQS_AD5P_35 Sch=pio[06]
set_property -dict { PACKAGE_PIN A15   IOSTANDARD LVCMOS33 } [get_ports { teachee_led[1]  }]; #IO_L6N_T0_VREF_16 Sch=pio[07]
set_property -dict { PACKAGE_PIN B15   IOSTANDARD LVCMOS33 } [get_ports { ftdi_siwu_n  }]; #IO_L11N_T1_SRCC_16 Sch=pio[08]
set_property -dict { PACKAGE_PIN A14   IOSTANDARD LVCMOS33 } [get_ports { ftdi_wr_n  }]; #IO_L6P_T0_16 Sch=pio[09]
set_property -dict { PACKAGE_PIN J3    IOSTANDARD LVCMOS33 } [get_ports { ftdi_rd_n }]; #IO_L7P_T1_AD6P_35 Sch=pio[10]
set_property -dict { PACKAGE_PIN J1    IOSTANDARD LVCMOS33 } [get_ports { ftdi_rxf_n }]; #IO_L3N_T0_DQS_AD5N_35 Sch=pio[11]
set_property -dict { PACKAGE_PIN K2    IOSTANDARD LVCMOS33 } [get_ports { hsadc_a[7] }]; #IO_L5P_T0_AD13P_35 Sch=pio[12]
set_property -dict { PACKAGE_PIN L1    IOSTANDARD LVCMOS33 } [get_ports { hsadc_a[6] }]; #IO_L6N_T0_VREF_35 Sch=pio[13]
set_property -dict { PACKAGE_PIN L2    IOSTANDARD LVCMOS33 } [get_ports { hsadc_a[5] }]; #IO_L5N_T0_AD13N_35 Sch=pio[14]
set_property -dict { PACKAGE_PIN M1    IOSTANDARD LVCMOS33 } [get_ports { hsadc_a[4] }]; #IO_L9N_T1_DQS_AD7N_35 Sch=pio[17]
set_property -dict { PACKAGE_PIN N3    IOSTANDARD LVCMOS33 } [get_ports { hsadc_a[3] }]; #IO_L12P_T1_MRCC_35 Sch=pio[18]
set_property -dict { PACKAGE_PIN P3    IOSTANDARD LVCMOS33 } [get_ports { hsadc_a[2] }]; #IO_L12N_T1_MRCC_35 Sch=pio[19]
set_property -dict { PACKAGE_PIN M2    IOSTANDARD LVCMOS33 } [get_ports { hsadc_a[1] }]; #IO_L9P_T1_DQS_AD7P_35 Sch=pio[20]
set_property -dict { PACKAGE_PIN N1    IOSTANDARD LVCMOS33 } [get_ports { hsadc_a[0] }]; #IO_L10N_T1_AD15N_35 Sch=pio[21]
set_property -dict { PACKAGE_PIN N2    IOSTANDARD LVCMOS33 } [get_ports { spare_pin[0] }]; #IO_L10P_T1_AD15P_35 Sch=pio[22]
set_property -dict { PACKAGE_PIN P1    IOSTANDARD LVCMOS33 } [get_ports { spare_pin[1] }]; #IO_L19N_T3_VREF_35 Sch=pio[23]
set_property -dict { PACKAGE_PIN R3    IOSTANDARD LVCMOS33 } [get_ports { hsadc_b[7] }]; #IO_L2P_T0_34 Sch=pio[26]
set_property -dict { PACKAGE_PIN T3    IOSTANDARD LVCMOS33 } [get_ports { hsadc_b[6] }]; #IO_L2N_T0_34 Sch=pio[27]
set_property -dict { PACKAGE_PIN R2    IOSTANDARD LVCMOS33 } [get_ports { hsadc_b[5] }]; #IO_L1P_T0_34 Sch=pio[28]
set_property -dict { PACKAGE_PIN T1    IOSTANDARD LVCMOS33 } [get_ports { hsadc_b[4] }]; #IO_L3P_T0_DQS_34 Sch=pio[29]
set_property -dict { PACKAGE_PIN T2    IOSTANDARD LVCMOS33 } [get_ports { hsadc_b[3] }]; #IO_L1N_T0_34 Sch=pio[30]
set_property -dict { PACKAGE_PIN U1    IOSTANDARD LVCMOS33 } [get_ports { hsadc_b[2] }]; #IO_L3N_T0_DQS_34 Sch=pio[31]
set_property -dict { PACKAGE_PIN W2    IOSTANDARD LVCMOS33 } [get_ports { hsadc_b[1] }]; #IO_L5N_T0_34 Sch=pio[32]
set_property -dict { PACKAGE_PIN V2    IOSTANDARD LVCMOS33 } [get_ports { hsadc_b[0] }]; #IO_L5P_T0_34 Sch=pio[33]
set_property -dict { PACKAGE_PIN W3    IOSTANDARD LVCMOS33 } [get_ports { spare_pin[3] }]; #IO_L6N_T0_VREF_34 Sch=pio[34]
set_property -dict { PACKAGE_PIN V3    IOSTANDARD LVCMOS33 } [get_ports { spare_pin[2] }]; #IO_L6P_T0_34 Sch=pio[35]
set_property -dict { PACKAGE_PIN W5    IOSTANDARD LVCMOS33 } [get_ports { hsadc_a_enc }]; #IO_L12P_T1_MRCC_34 Sch=pio[36]
set_property -dict { PACKAGE_PIN V4    IOSTANDARD LVCMOS33 } [get_ports { spare_pin[5] }]; #IO_L11N_T1_SRCC_34 Sch=pio[37]
set_property -dict { PACKAGE_PIN U4    IOSTANDARD LVCMOS33 } [get_ports { spare_pin[4] }]; #IO_L11P_T1_SRCC_34 Sch=pio[38]
set_property -dict { PACKAGE_PIN V5    IOSTANDARD LVCMOS33 } [get_ports { ftdi_txe_n }]; #IO_L16N_T2_34 Sch=pio[39]
set_property -dict { PACKAGE_PIN U5    IOSTANDARD LVCMOS33 } [get_ports { ftdi_data[0] }]; #IO_L16P_T2_34 Sch=pio[41]
set_property -dict { PACKAGE_PIN U2    IOSTANDARD LVCMOS33 } [get_ports { ftdi_data[1] }]; #IO_L9N_T1_DQS_34 Sch=pio[42]
set_property -dict { PACKAGE_PIN W6    IOSTANDARD LVCMOS33 } [get_ports { ftdi_data[2] }]; #IO_L13N_T2_MRCC_34 Sch=pio[43]
set_property -dict { PACKAGE_PIN U3    IOSTANDARD LVCMOS33 } [get_ports { ftdi_data[3] }]; #IO_L9P_T1_DQS_34 Sch=pio[44]
set_property -dict { PACKAGE_PIN U7    IOSTANDARD LVCMOS33 } [get_ports { ftdi_data[4] }]; #IO_L19P_T3_34 Sch=pio[45]
set_property -dict { PACKAGE_PIN W7    IOSTANDARD LVCMOS33 } [get_ports { ftdi_data[5] }]; #IO_L13P_T2_MRCC_34 Sch=pio[46]
set_property -dict { PACKAGE_PIN U8    IOSTANDARD LVCMOS33 } [get_ports { ftdi_data[6] }]; #IO_L14P_T2_SRCC_34 Sch=pio[47]
set_property -dict { PACKAGE_PIN V8    IOSTANDARD LVCMOS33 } [get_ports { ftdi_data[7] }]; #IO_L14N_T2_SRCC_34 Sch=pio[48]

## UART
#set_property -dict { PACKAGE_PIN J18   IOSTANDARD LVCMOS33 } [get_ports { uart_rxd_out }]; #IO_L7N_T1_D10_14 Sch=uart_rxd_out
#set_property -dict { PACKAGE_PIN J17   IOSTANDARD LVCMOS33 } [get_ports { uart_txd_in  }]; #IO_L7P_T1_D09_14 Sch=uart_txd_in

## Crypto 1 Wire Interface
#set_property -dict { PACKAGE_PIN D17   IOSTANDARD LVCMOS33 } [get_ports { crypto_sda }]; #IO_0_14 Sch=crypto_sda

## QSPI
#set_property -dict { PACKAGE_PIN K19   IOSTANDARD LVCMOS33 } [get_ports { qspi_cs    }]; #IO_L6P_T0_FCS_B_14 Sch=qspi_cs
#set_property -dict { PACKAGE_PIN D18   IOSTANDARD LVCMOS33 } [get_ports { qspi_dq[0] }]; #IO_L1P_T0_D00_MOSI_14 Sch=qspi_dq[0]
#set_property -dict { PACKAGE_PIN D19   IOSTANDARD LVCMOS33 } [get_ports { qspi_dq[1] }]; #IO_L1N_T0_D01_DIN_14 Sch=qspi_dq[1]
#set_property -dict { PACKAGE_PIN G18   IOSTANDARD LVCMOS33 } [get_ports { qspi_dq[2] }]; #IO_L2P_T0_D02_14 Sch=qspi_dq[2]
#set_property -dict { PACKAGE_PIN F18   IOSTANDARD LVCMOS33 } [get_ports { qspi_dq[3] }]; #IO_L2N_T0_D03_14 Sch=qspi_dq[3]
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

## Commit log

2022-11-12 TeachEE PCB Design (#1)
    * add initial pcb design files and hardware git ignore
    * swap out FTDI memory for a part that is in stock
    * schematic error clean up
    * switch to simpler 2 channel ADC
    * partial placement of the PCB
    * finish component placement
    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
    [ADC.SchDoc, AFE.SchDoc, AFE_DIFF.SchDoc, Bittele_Initial_DFM_Check_Report_8013074A1_2022-10-27_Answers.xls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]
2022-11-13 Add Mitigation Strategy Table (#11)
    * add mitigation strategy table
    * update pcb layout comment
2022-12-19 FPGA Project Template (#29)
    * initial blink project, still need to mode the structure but this saves my progress thus far
    * note: this is a sample project
2022-12-24 FTDI Example and Test (#30)
    * init ftdi example project. Want to build an echo program and test the FIFO functionality on the PCB
    * add ftdi pin constraints
    * get fpga hooked up to ftdi fifo clock
    * receive characters from FPGA through FTDI chip on TeachEE pcb
    * add reset sync
    * add ILA for reset debug
    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
2022-12-28 CMOD XADC Example (#33)
    * create base project for XADC example
    * add constraints for adc inputs
    * add xadc top level module (templated off ftdi_sync)
    * add ADC instance template and generate IP within xpr
    * start wiring up the xadc module, write some notes
    * initial draft of the xadc bfm
    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
2023-01-05 add tray cad and readme (#60)
    [teachee_tray.f3d, teachee_tray.f3z]
2023-01-15 Design and implement generic sample consumption (#20)
    * Design and implement generic sample consumption
    - Created trait sample_source::SampleSource
    - Created two implementations of SampleSource
    - FtSampleSource: WIP, reads data from a real TeachEE
    - SineSampleSource: Puts a genrated sine wave onto VoltageA channel,
    useful for testing
    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
2023-01-29 COBS Encoder Wrapper (#74)
    * start work on a wrapper for cobs encode module
    * start skeleton of a testbench, see if it passes CI
    * play around with test case syntax
    * completed primitive cobs encoder tb
    * rename test case
    * save changes before refactor
    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
2023-01-31 XADC 16-bit to 8-bit AXIS Stream Adapter (#69)
    * start on cobs packets for xadc
    * set up module interface and package
    * save changes on packetizer
    * start integrating packetizer with cobs encoder
    * continue work on the state machine before dinner
    * first draft of COBS packetizer state machine
    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
2023-02-05 COBS Encoder Refactor (#78)
    * First magit commit!
    * cobs encoder stuff and git ignore updates
    * make editor related ignores global
    * debugging away, no luck yet. Going to try and see what is up with an ILA. No alignment between sim and reality rn
    * cobs appears to be working! Might have been an issue with don't care bits on the tkeep signal
    * add emacs ignore to top level git ignore
    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
2023-02-08 XADC Stream Cleanup (#79)
    * initial commit to clean junk data from the XADC packets
    * Add defines for XADC sample start and end indices
    * CI fixup, remove packet package ref from TB
    * fix testbench to reflect packetizer changes
2023-02-25 Divide data processing between 3 threads (#83)
    * Add thread to control buffer data flow between App and USB
    * Use condition variables to synchronize
    * Refactor, add triggering
    * Change buffers to hold voltage and current buffers
    * Decode bytes
    * decode with cobs
    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
2023-03-04 Use new packet format (#90)
    * Use new packet format
    New packet format is the old one but sample bytes are reversed. Also
    scale current samples properly.
    * Add Eric's code from in-person work session
    * Make decoder more tolerant of bad packets
    * invalid packet skip fix from work session w Eric
    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
2023-03-07 Fix triggering and add one for channel 2 (#95)
    Fix triggering not returning the correct number of samples, and add a
    second trigger for channel 2.
2023-03-17 Implement FFT (#118)
    * Implement FFT
    Closes: #87
    * Adjust spectrum analyzer params
    * Fix latency by increasing samples read
    * Move constant
    * Cleanup
    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
2023-03-18 Final Report Hardware Verification Section (#120)
    * add spec eval tables and start hw verification section
    * add draft of functional tests
    * add pcb front and back figures
    * add closeup and final assembly figures
    * move sections per Eric's suggestion
    * fixup units and use SIunitx
2023-04-06 shorten code samples, shrink figures (#141)
2023-04-08 Full pass edit (#146)
    * Full pass edit
    * Cut to 49 pages
    * Fix spacing
    * Spelling
    * Review
    ---------
